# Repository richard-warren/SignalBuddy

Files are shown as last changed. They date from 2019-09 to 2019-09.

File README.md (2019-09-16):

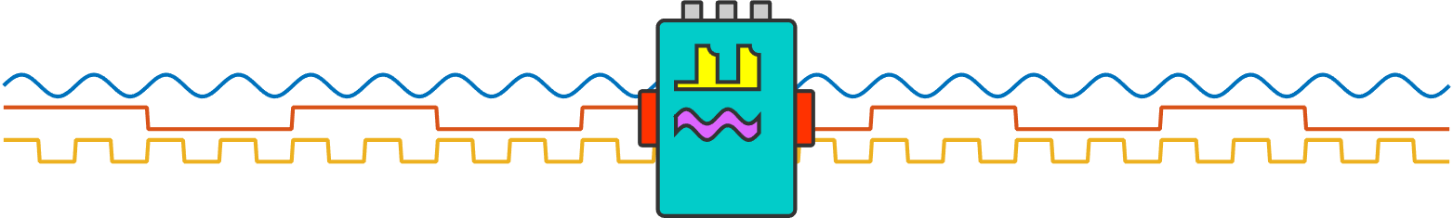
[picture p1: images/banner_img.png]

# SignalBuddy
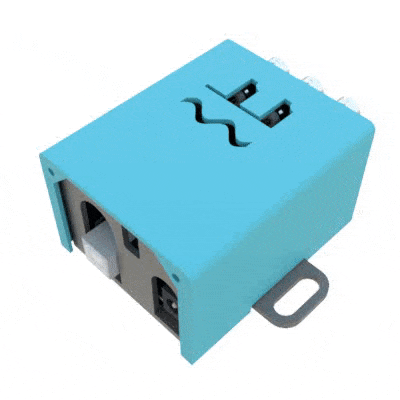
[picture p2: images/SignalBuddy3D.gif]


`SignalBuddy` is an easy-to-make, easy-to-use signal generator for scientific applications. Making friends is hard, but making `SignalBuddy` is easy. All you need is an Arduino Uno! `SignalBuddy` replaces more complicated and (much) more expensive signal generators in laboratory settings where one millisecond resolution is sufficient. `SignalBuddy` can:

* generate **sin waves**, **step functions**, and **pulse trains**
* generate **DIGITAL** and **PWM** signals, in addition to **TRUE ANALOG** signals when used with the optional [MCP4725 Chip](https://www.adafruit.com/product/935)  
* be controlled with an intuitive serial monitor interface
* look fabulous is an optional 3D printed enclosure

Here are recordings of signals generated by SignalBuddy:

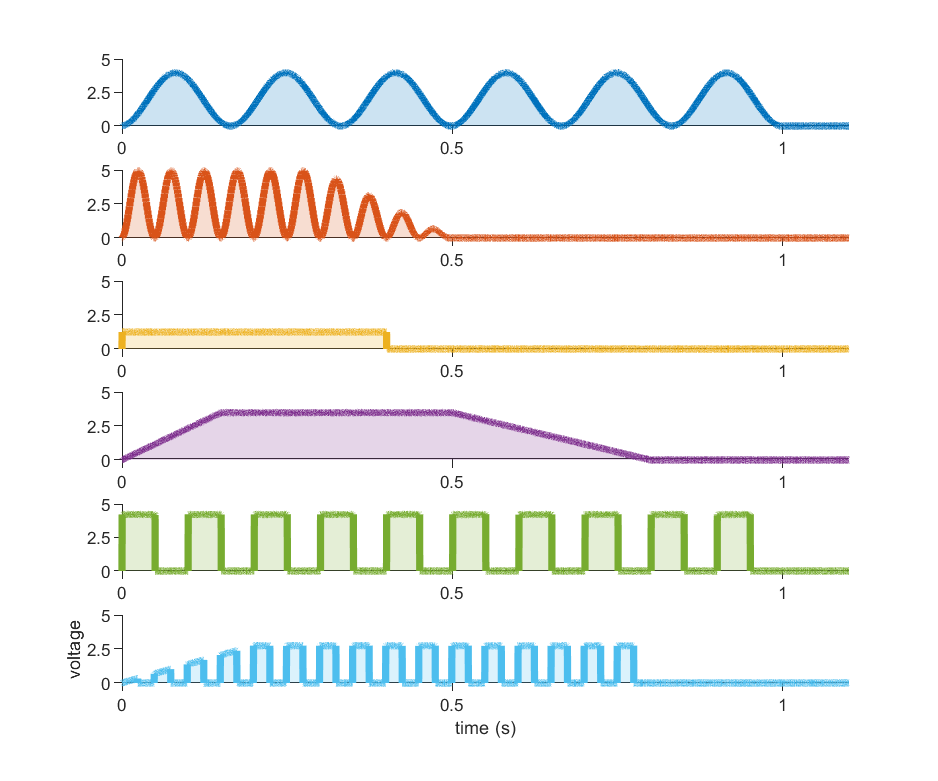
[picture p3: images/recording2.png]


## quick start
* Download this repository, open `SignalBuddy.ino` from the `SignalBuddy` folder, and [upload it to an Arduino Uno using the Arduino IDE](https://www.arduino.cc/en/main/howto).
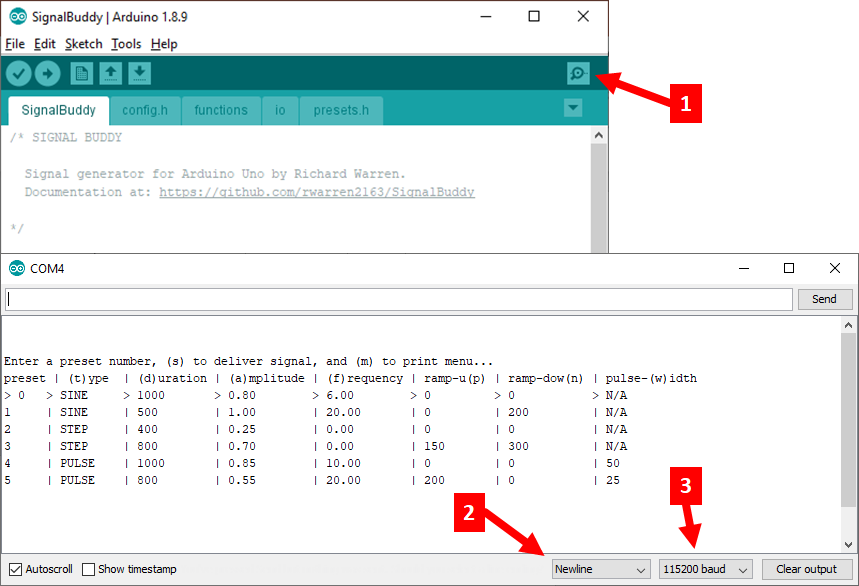
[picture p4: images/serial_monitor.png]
* Open the Serial Monitor by clicking the button in the top right of the IDE (1). Make sure the line ending dropdown is set to 'Newline' (2) and the baud rate is set to 115200 (3).<br/><br/><br/><br/>
* Enter **a number** to change the preset, **s** to deliver a signal, and **m** to print the menu. Presets can be adjusted by entering the letters in parentheses. For example, enter **a** to change the amplitude, **p** to change the ramp up time, and **f** to change the frequency of the currently selected stimulus.
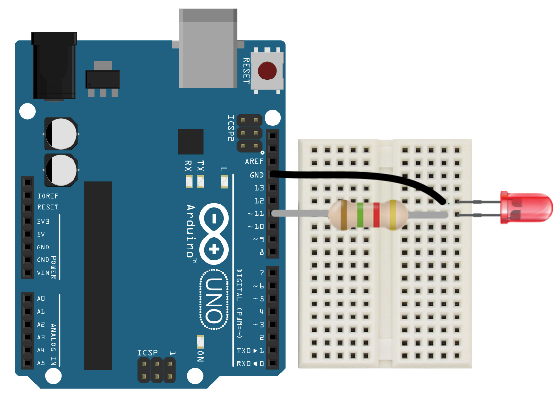
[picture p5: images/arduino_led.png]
* The PWM / digital signal is delivered from **PIN 11**. To visualize the signal, put a resistor (~100 ohm) + LED between pin 11 and ground. Connect the long leg of the LED to pin 11, and the short leg to ground:<br/>

## true analog output
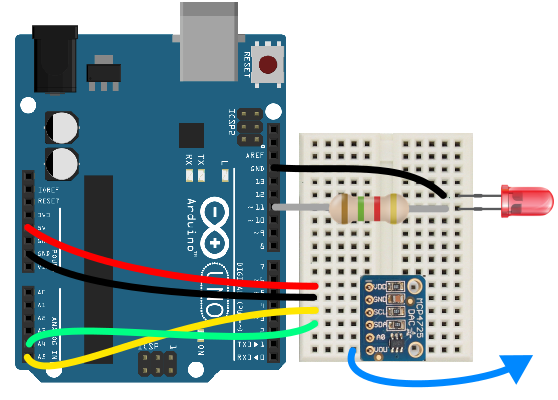
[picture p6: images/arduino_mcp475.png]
The amplitude of pin 11 output is modulated using [Pulse Width Modulation (PWM)](https://www.arduino.cc/en/tutorial/PWM) - basically, the output oscillates rapidly between 0 and 5 volts to approximate voltage between 0 and 5. `SignalBuddy` can generate true analog output when used with the [MCP4725 Chip](https://www.adafruit.com/product/935). Simply wire things up like this:<br/>

Now the **VOUT** pin outputs an analog version of the signal. Notice that the PWM output can be used simultaneously. In my experiments I use pin 11 to drive a reference LED that is captured in a video feed, while the analog output drives a laser for optogenetics experiments.

## external triggering
Signals can be triggered by an external TTL input (a 5V pulse) to **PIN 2**. Simply change the `externalTrigger` parameter in `config.h` to `true` and re-upload the script. Now the currently selected preset will be delivered when the input on pin 2 changes from 0 to 5 volts.

## custom presets
You can adjust / add up to 9 presets by modifying `config.h` and re-uploading the script. Your new presets will appear when you re-open the Serial Monitor.

## project box
You can 3D print a custom `SignalBuddy` enclosure using the .stl files in the `enclosure` folder (see 3D animation above). The box is easily mountable, has a snap fit design for both the Arduino and the lid (no screws necessary!), and has convenient BNC ports. More details are available on the [SignalBuddy hackaday page](https://hackaday.io/project/167649-signalbuddy). Here is `SignalBuddy` making friends with Lindsey Buckingham:

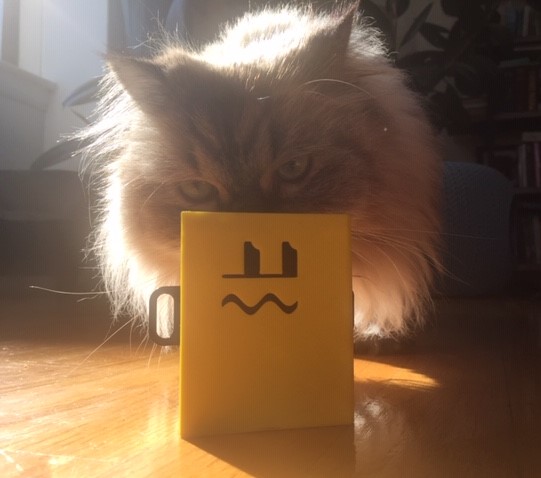
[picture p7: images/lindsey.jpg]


## how the code works
There are a few neat tricks that make the signals accurate and the interface easy to use:

* [Timer interrupts](https://www.instructables.com/id/Arduino-Timer-Interrupts/) are at the heart of the code. The idea is this: Arduino Unos have 3 timers that can trigger blocks of code at user-specified frequencies. `SignalBuddy` sets timer 0 to 1 kHz, which triggers code that updates the signal every 1 millisecond. Using timer interrupts can be a little tricky, because several common Arduino functions rely on interrupts. For example, different PWM pins rely on different timers. It was important in this code to pick an output pin (pin 11) with PWM functionality that doesn't depend on the timer that's used for signal generation (timer 0).

* Rather than doing trigonometry on the fly, I use a sine lookup table to generate sine waves. But a long sine table eats up a ton of memory! It turns out that Arduino uses two types of memory: SRAM and flash. By default, programs are uploaded to SRAM memory, which is quite small. You can use [PROGMEM](https://www.arduino.cc/reference/en/language/variables/utilities/progmem/) to store variables in flash with little cost in terms of access speed. Another great trick is to use [the F macro](https://forum.arduino.cc/index.php?topic=110307.0) to save text printed to the Serial port to flash, rather than saving all of that text (one byte per letter!) to SRAM.

* This is my first object oriented Arduino project. Taking an object oriented approach was a real organizational game changer. Now I can't imagine the code working any other way! Each user preset is an instance of a Preset class, which has attributes ('members' in C++ terminology) such as amplitude, frequency, etc. All the presets can be easily stored and accessed in an array. Awesome.

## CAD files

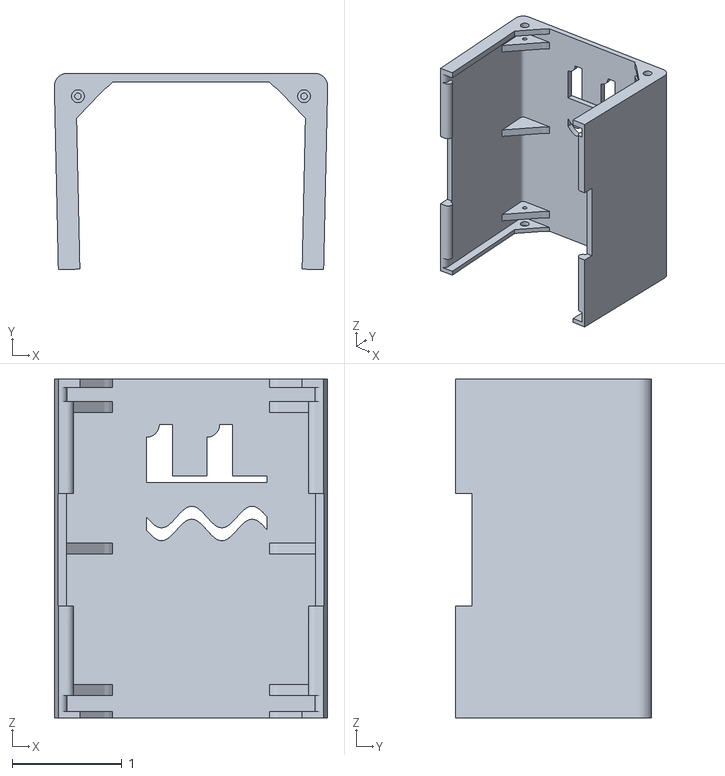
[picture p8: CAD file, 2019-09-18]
enclosure/lid.stl
2.49 x 1.79 x 3.09

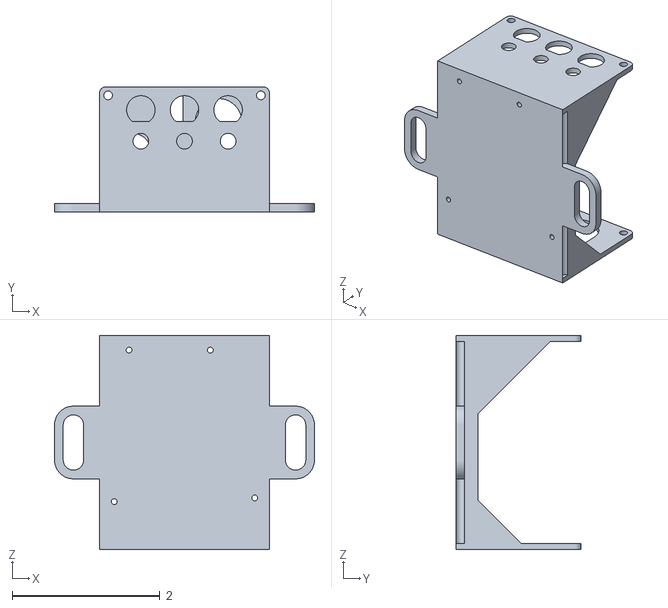
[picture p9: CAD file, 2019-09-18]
enclosure/base.stl
3.52 x 1.69 x 2.90

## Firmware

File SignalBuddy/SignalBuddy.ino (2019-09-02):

/* SIGNAL BUDDY

  Signal generator for Arduino Uno by Richard Warren.
  Documentation at: https://github.com/rwarren2163/SignalBuddy
  
*/



// initializations
enum signalType {SINE, STEP, PULSE, UNSET};
const String signalNames[] = {"SINE", "STEP", "PULSE"};

#include "Adafruit_MCP4725.h"
#include "presets.h"

const int triggerPin = 2; // pin that triggers stimulation (must be an interrupt pin on Arduino Uno)
const int ledPin = 11; // don't change (can't use PWM pins that rely on timer0, which is hijacked in this script) // PWM output pins that delivers signal modulated the same as DAC, but scaled from 0-5V (use this to power a reference LED that can be captured in videos, for example)

const uint8_t PROGMEM sineLookup[] = {0, 0, 0, 0, 0, 0, 0, 0, 1, 1, 1, 1, 1, 2, 2, 2, 3, 3, 3, 4, 4, 4, 5, 5, 6, 6, 7, 7, 8, 8, 9, 10, 10, 11, 11, 12, 13, 14, 14, 15, 16, 17, 17, 18, 19, 20, 21, 22, 22, 23, 24, 25, 26, 27, 28, 29, 30, 31, 32, 33, 35, 36, 37, 38, 39, 40, 41, 43, 44, 45, 46, 47, 49, 50, 51, 53, 54, 55, 56, 58, 59, 61, 62, 63, 65, 66, 67, 69, 70, 72, 73, 75, 76, 78, 79, 81, 82, 84, 85, 87, 88, 90, 91, 93, 94, 96, 97, 99, 100, 102, 104, 105, 107, 108, 110, 112, 113, 115, 116, 118, 119, 121, 123, 124, 126, 127, 129, 131, 132, 134, 136, 137, 139, 140, 142, 143, 145, 147, 148, 150, 151, 153, 155, 156, 158, 159, 161, 162, 164, 165, 167, 168, 170, 171, 173, 174, 176, 177, 179, 180, 182, 183, 185, 186, 188, 189, 190, 192, 193, 194, 196, 197, 199, 200, 201, 202, 204, 205, 206, 208, 209, 210, 211, 212, 214, 215, 216, 217, 218, 219, 220, 222, 223, 224, 225, 226, 227, 228, 229, 230, 231, 232, 233, 233, 234, 235, 236, 237, 238, 238, 239, 240, 241, 241, 242, 243, 244, 244, 245, 245, 246, 247, 247, 248, 248, 249, 249, 250, 250, 251, 251, 251, 252, 252, 252, 253, 253, 253, 254, 254, 254, 254, 254, 255, 255, 255, 255, 255, 255, 255, 255, 255, 255, 255, 255, 255, 255, 255, 254, 254, 254, 254, 254, 253, 253, 253, 252, 252, 252, 251, 251, 251, 250, 250, 249, 249, 248, 248, 247, 247, 246, 245, 245, 244, 244, 243, 242, 241, 241, 240, 239, 238, 238, 237, 236, 235, 234, 233, 233, 232, 231, 230, 229, 228, 227, 226, 225, 224, 223, 222, 220, 219, 218, 217, 216, 215, 214, 212, 211, 210, 209, 208, 206, 205, 204, 202, 201, 200, 199, 197, 196, 194, 193, 192, 190, 189, 188, 186, 185, 183, 182, 180, 179, 177, 176, 174, 173, 171, 170, 168, 167, 165, 164, 162, 161, 159, 158, 156, 155, 153, 151, 150, 148, 147, 145, 143, 142, 140, 139, 137, 136, 134, 132, 131, 129, 128, 126, 124, 123, 121, 119, 118, 116, 115, 113, 112, 110, 108, 107, 105, 104, 102, 100, 99, 97, 96, 94, 93, 91, 90, 88, 87, 85, 84, 82, 81, 79, 78, 76, 75, 73, 72, 70, 69, 67, 66, 65, 63, 62, 61, 59, 58, 56, 55, 54, 53, 51, 50, 49, 47, 46, 45, 44, 43, 41, 40, 39, 38, 37, 36, 35, 33, 32, 31, 30, 29, 28, 27, 26, 25, 24, 23, 22, 22, 21, 20, 19, 18, 17, 17, 16, 15, 14, 14, 13, 12, 11, 11, 10, 10, 9, 8, 8, 7, 7, 6, 6, 5, 5, 4, 4, 4, 3, 3, 3, 2, 2, 2, 1, 1, 1, 1, 1, 0, 0, 0, 0, 0, 0, 0};
const int sineSmps = sizeof(sineLookup);
volatile uint8_t currentPreset = 0;
volatile float sineIndex = 0;
volatile float bitConversion = 4095 / 255;
volatile bool updated = false; // keeps track of whether the desired value for the ADC has been updated
volatile uint8_t oldValue = 0;
volatile uint8_t newValue = 0;
volatile long signalTimer = 0;  // timer for the duration of the signal
volatile long pulseTimer = 0; // keeps track of interstimulus interval in the pulse condition
volatile bool isSignalOn = false;
volatile char inputChar;
volatile int inputInt;
volatile float inputFloat;
int maxPulseWidth;
bool presetChanged;
String inputString;
char inputBuffer[100];
bool externalTrigger;
bool constantSignalDuration;
bool ledAmplitudeScaling;
Adafruit_MCP4725 dac;
Preset presets[9];
volatile float deltaIndex; // how far to advance in the lookup table for every clock tick
volatile float interPulseInterval;




void setup() {

  // load user configuration
#include "config.h"
  updateFrequency();  // sets global variables that depend on current present stimulus frequency

  // initialize pins
  pinMode(triggerPin, INPUT);
  pinMode(ledPin, OUTPUT);
  analogWrite(ledPin, 0);

  // initialize timer0 interrupt
  cli();//disable interrupts
  TCCR0A = 0;// set entire TCCR0A register to 0
  TCCR0B = 0;// same for TCCR0B
  TCNT0  = 0;//initialize counter value to 0
  OCR0A = 249; // set compare match register for 2khz increments
  TCCR0A |= (1 << WGM01); // turn on CTC mode
  TCCR0B |= (1 << CS01) | (1 << CS00); // Set CS01 and CS00 bits for 64 prescaler
  TIMSK0 |= (1 << OCIE0A); // enable timer compare interrupt
  sei();//enable interrupts

  // initialize DAC
  TWBR = 12; // speed up i2c communication
  dac.begin(0x62); // begin communication with DAC
  dac.setVoltage(0, false);
  if (externalTrigger) {
    attachInterrupt(digitalPinToInterrupt(triggerPin), signalOnOff, CHANGE);
  }

  // initialize serial communication
  Serial.begin(115200);
  while (!Serial) {}; // wait for serial port to connect
  showMenu();
}



void loop() {

  // update LED output if value has changed
  if (updated) {
    if (ledAmplitudeScaling){
      analogWrite(ledPin, newValue * presets[currentPreset].amplitude);
    }else{
      analogWrite(ledPin, newValue);
    }
    dac.setVoltage(constrain(round(newValue * bitConversion * presets[currentPreset].amplitude), 0, 4095), false);
    updated = false;
  }

  getUserInput();
}

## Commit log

2019-09-14 added 3D printed enclosure files
    [base.stl, lid.stl]
2019-09-18 deleted old cad files
    [base.stl, lid.stl]
2019-09-18 updated cad files
    [base.stl, lid.stl]
